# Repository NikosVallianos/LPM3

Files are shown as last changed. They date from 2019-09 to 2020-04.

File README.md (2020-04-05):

# LPM3 front-end #

The LPM3 is a device to measure light pollution on sea turtle nesting beaches. This repository focuses on the development of the front-end of the device, which can be used separately by any programmable device with an I²C and a SPI interface, such as an arduino, raspberry pi, or a suitable USB adapter.

The LPM3 front-end consists of a high sensitivity photometer and a regular sensitivity single-chip lux meter, an accelerometer, and a magnetometer all laid out on a single printed circuit board.

## Ultra-low dark current photodiode

The core of the LPM3 front-end is Hamamatsu's S1133, an ultra-low dark current visible light photodiode. A transimpedance amplifier with a 1GOhm feedback resistor gives a theoretical output of 1V per 0.164 lux. With a 12-bit ADC and a 2.5V reference, we can get a sensitivity of 0.0001 lux. The LPM3 is equipped with a 16-bit ADC, giving an absurd theoretical sensitivity of 0.00000625lux. Imperfections in the circuits and component manufacturing are expected to 

## Generic lux meter

The high sensitivity photodiode circuit is unable to measure any illuminance higher than 0.41lux. For this reason, and to serve as a crude source of self-calubration reference, the OPT3001 single-chip lux meter by Texas Instruments was incorporated in the LPM3 font-end. This lux meter is capable of measurements from 0.01 lux all the way up to daylight. This should cover all foreseeable light pollution conditions from pitch black all the way to in front of spotlights that are sometimes used to safeguard beach equipment.

## Accelerometer

All light pollution measurements should be taken at a horizontal plane, which is where hatchlings and sea turtles scan to perceive ambient light. An embedded accelerometer can either ensure this condition or be used to include device orientation in the dataset.

## Magnetometer

A magnetometer is the only way to know what direction a specific light pollution measurement was taken from.

## License
The LPM3 depository integrates hardware design, firmware source code, desktop software, and supporting documentation. These are licensed as follows:
- Hardware design files are licensed under the CERN Open Hardware License,
- Software source code files are licensed under the GNU GPL v3 license,
- Documentation files are licensed under the GNU Free Documentation License,
- Videos are licensed under Creative Commons Attribution-ShareAlike 4.0 International.

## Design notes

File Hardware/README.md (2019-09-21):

This folder contains the hardware PCB design files, bill of materials, notes, data sheet links, and other details to help you manufacture a LPM3.
The hardware elements of the LPM3 project are licensed under the CERN Open Source Hardware license found here (link missing).

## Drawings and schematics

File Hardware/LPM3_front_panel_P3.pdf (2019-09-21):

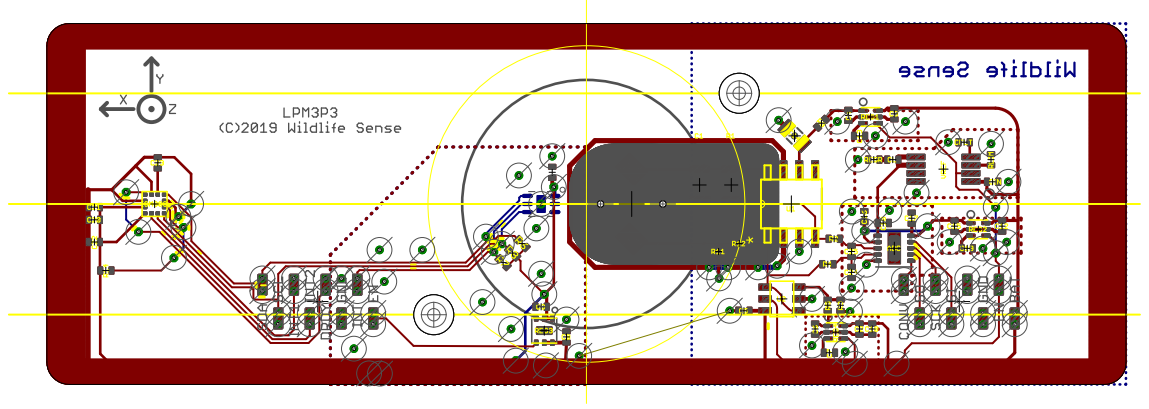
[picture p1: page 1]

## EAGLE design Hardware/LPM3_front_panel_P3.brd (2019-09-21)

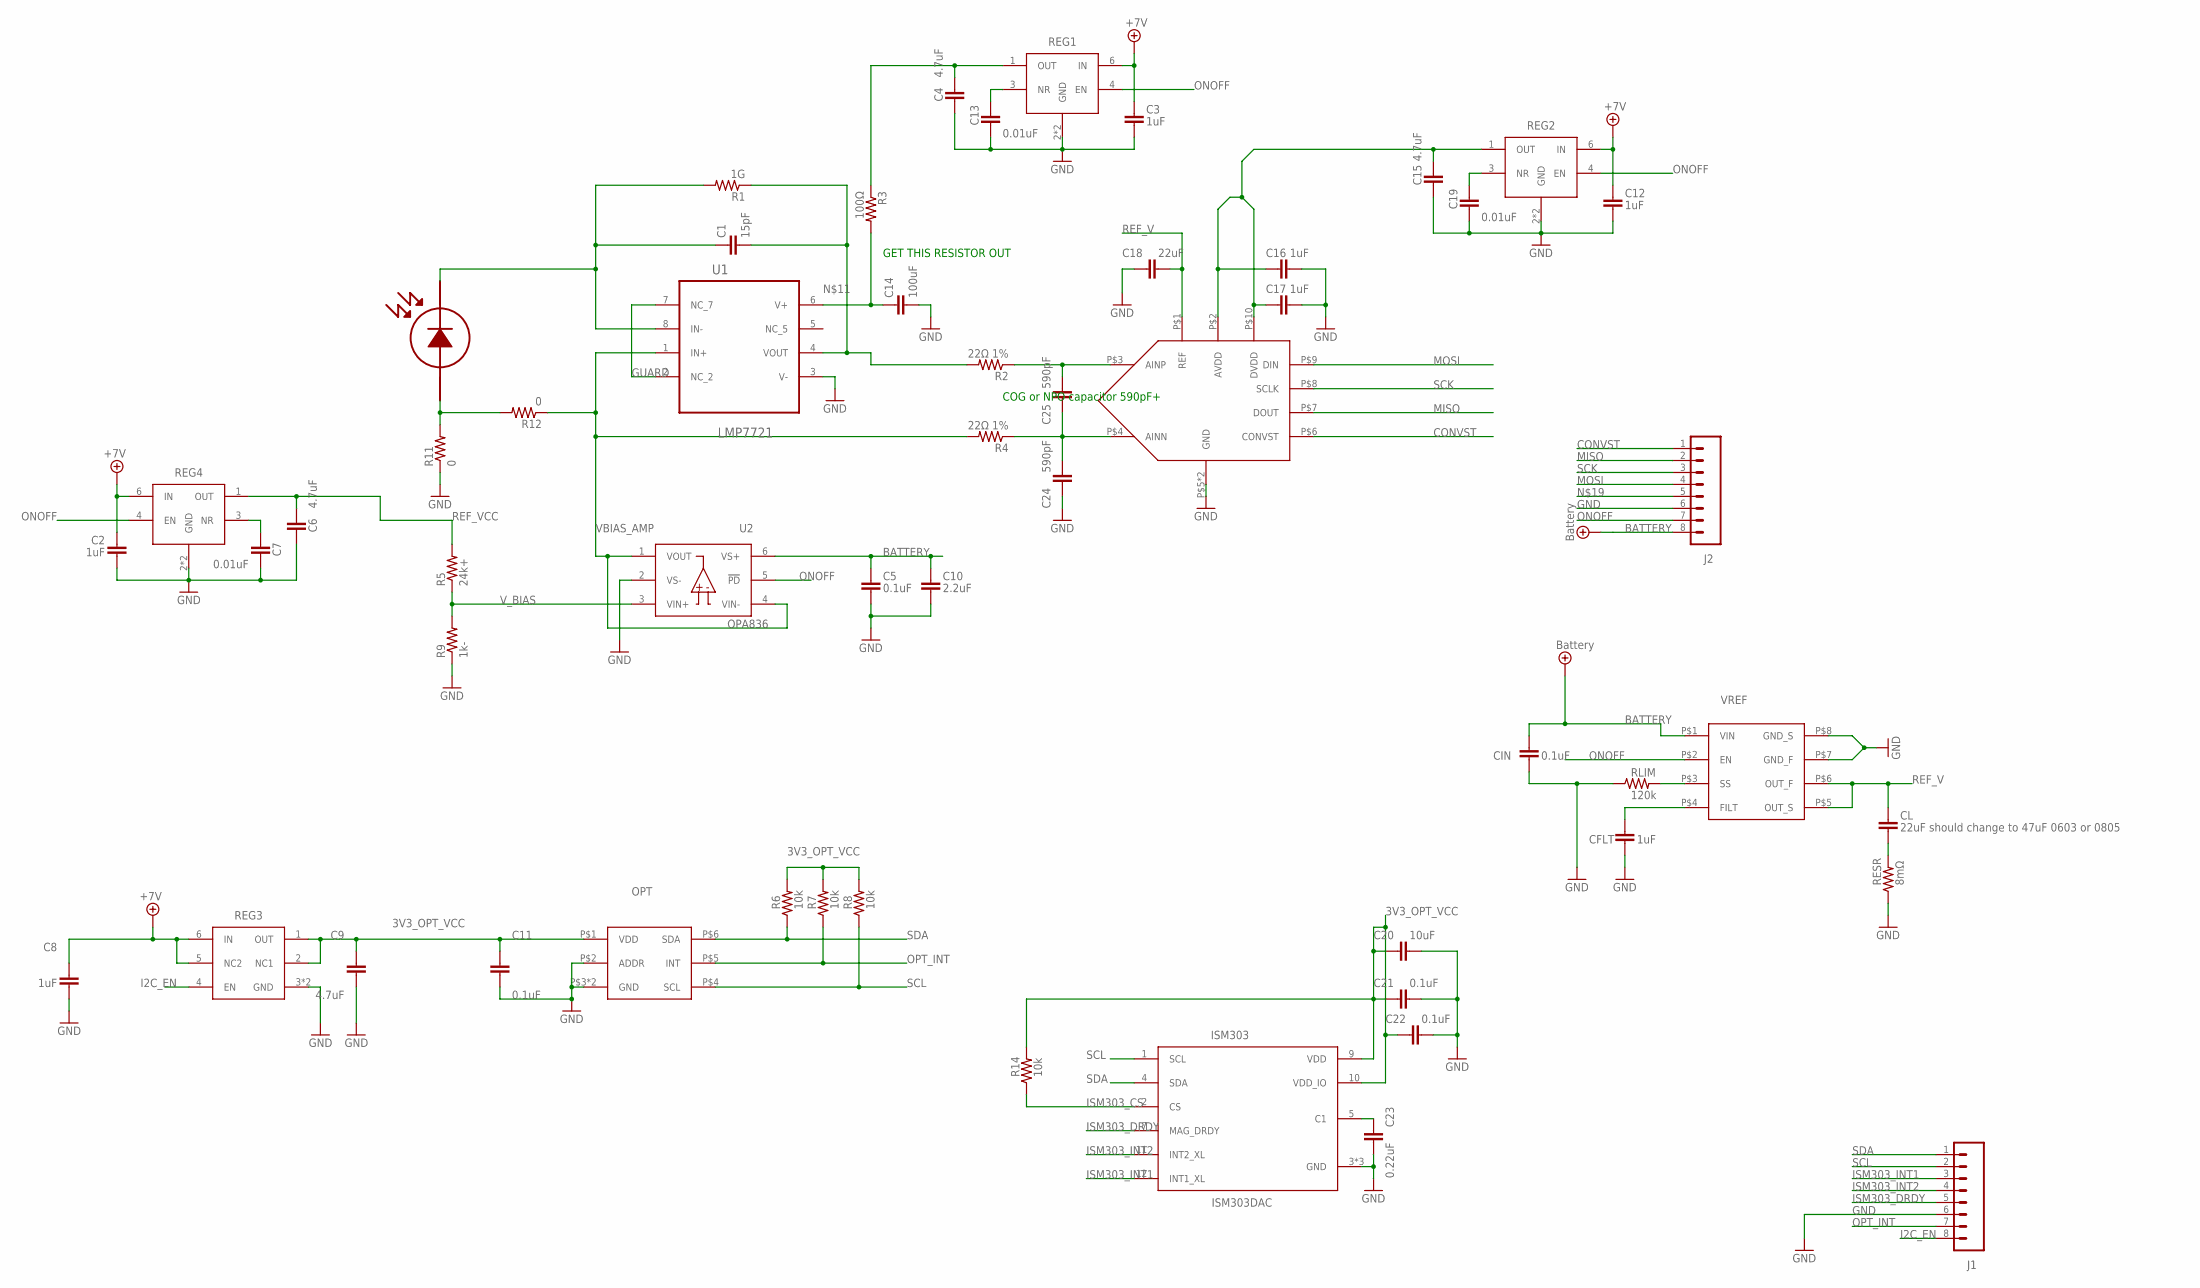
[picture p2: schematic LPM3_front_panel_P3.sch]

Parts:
ADC: ADS8866VSON10; VSON-10
C1: 15pF; 1206
C2, C3, C8, C12, C16, C17: 1uF; SMD_0402
C4, C6, C9, C15: 4.7uF; SMD_0402
C5, C11, C21, C22: 0.1uF; SMD_0402
C7, C13, C19: 0.01uF; SMD_0402
C10: 2.2uF; SMD_0402
C14: 100uF; 0805-CAP
C18: 22uF; SMD_0402
C20: 10uF; SMD_0402
C23: 0.22uF; SMD_0402
C24, C25: 590pF; SMD_0402
CFLT: 1uF; SMD_0402
CIN: 0.1uF; SMD_0402
CL: 22uF should change to 47uF 0603 or 0805; SMD_0402
D1: S1133_3; S1133_FLAT_SIDEWAYS
ISM303: ISM303DAC; LGA_12_ST
J1, J2: 8_PIN_0.05_INCH_SMD_FEMALE; 8_PIN_0.05"_SMD_ALTERN
OPT: OPT3001; USON-6-0.65-OPT3001
R1: 1G; 1206
R2, R4: 22Ω 1%; SMD_0402
R3: 100Ω; SMD_0402
R5: 24k+; SMD_0402
R6, R7, R8, R14: 10k; SMD_0402
R9: 1k-; SMD_0402
R11, R12: 0; SMD_0402
REG1, REG2, REG4: TPS717-Q1; WSON-6-1.5MM-NO-PAD
REG3: TPS706USON-6; USON-6-0.65
RESR: 8mΩ; SMD_0402
RLIM: 120k; SMD_0402
U1: LMP7721; SOIC127P600X175-8N
U2: OPA836; OPA836_SOT23
VREF: REF6225; VSSOP8

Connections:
3V3_OPT_VCC: C9.1, C11.1, C20.1, C21.1, C22.1, ISM303.9 (VDD), ISM303.10 (VDD_IO), OPT.P$1 (VDD), R6.1, R7.1, R8.1, R14.1, REG3.1 (OUT), REG3.2 (NC1)
BATTERY: C2.1, C3.1, C5.1, C8.1, C10.1, C12.1, CIN.1, J2.8, REG1.6 (IN), REG2.6 (IN), REG3.5 (NC2), REG3.6 (IN), REG4.6 (IN), U2.6 (VS+), VREF.P$1 (VIN)
CONVST: ADC.P$6 (CONVST), J2.1
FLT: CFLT.1, VREF.P$4 (FILT)
GND: ADC.P$5 (GND), ADC.P$PAD (GND), C2.2, C3.2, C4.2, C5.2, C6.2, C7.2, C8.2, C9.2, C10.2, C11.2, C12.2, C13.2, C14.2, C15.2, C16.2, C17.2, C18.1, C19.2, C20.2, C21.2, C22.2, C23.2, C24.1, CFLT.2, CIN.2, ISM303.3 (GND), ISM303.6 (GND), ISM303.8 (GND), J1.6, J2.6, OPT.P$2 (ADDR), OPT.P$3 (GND), OPT.PAD (GND), R9.2, R11.2, REG1.2 (GND), REG1.5 (GND), REG2.2 (GND), REG2.5 (GND), REG3.3 (GND), REG3.PAD (GND), REG4.2 (GND), REG4.5 (GND), RESR.2, RLIM.2, U1.3 (V-), U2.2 (VS-), VREF.P$7 (GND_F), VREF.P$8 (GND_S)
GUARD: U1.2 (NC_2), U1.7 (NC_7)
I2C_EN: J1.8, REG3.4 (EN)
ISM303_CS: ISM303.2 (CS), R14.2
ISM303_DRDY: ISM303.7 (MAG_DRDY), J1.5
ISM303_INT1: ISM303.12 (INT1_XL), J1.3
ISM303_INT2: ISM303.11 (INT2_XL), J1.4
MISO: ADC.P$7 (DOUT), J2.2
MOSI: ADC.P$9 (DIN), J2.4
unnamed: ADC.P$3 (AINP), C25.2, R2.2
unnamed: CL.2, RESR.1
unnamed: C1.P$1 (1), D1.CATHODE, R1.P$1 (1), U1.8 (IN-)
unnamed: C19.1, REG2.3 (NR)
unnamed: D1.ANODE, R11.1, R12.1
unnamed: C14.1, R3.1, U1.6 (V+)
unnamed: ADC.P$4 (AINN), C24.2, C25.1, R4.2
unnamed: C23.1, ISM303.5 (C1)
unnamed: C7.1, REG4.3 (NR)
unnamed: C13.1, REG1.3 (NR)
ONOFF: J2.7, REG1.4 (EN), REG2.4 (EN), REG4.4 (EN), U2.5 (!PD!), VREF.P$2 (EN)
OPAMP_VCC: C4.1, R3.2, REG1.1 (OUT)
OPT_INT: J1.7, OPT.P$5 (INT), R7.2
REF_V: ADC.P$1 (REF), C18.2, CL.1, VREF.P$5 (OUT_S), VREF.P$6 (OUT_F)
REF_VCC: C6.1, R5.1, REG4.1 (OUT)
SCK: ADC.P$8 (SCLK), J2.3
SCL: ISM303.1 (SCL), J1.2, OPT.P$4 (SCL), R8.2
SDA: ISM303.4 (SDA), J1.1, OPT.P$6 (SDA), R6.2
SS: RLIM.1, VREF.P$3 (SS)
TIA_OUT: C1.P$2 (2), R1.P$2 (2), R2.1, U1.4 (VOUT)
VBIAS_AMP: R4.1, R12.2, U1.1 (IN+), U2.1 (VOUT), U2.4 (VIN-)
VCC_ADC: ADC.P$2 (AVDD), ADC.P$10 (DVDD), C15.1, C16.1, C17.1, REG2.1 (OUT)
V_BIAS: R5.2, R9.1, U2.3 (VIN+)

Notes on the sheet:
GET THIS RESISTOR OUT
COG or NPO capacitor 590pF+

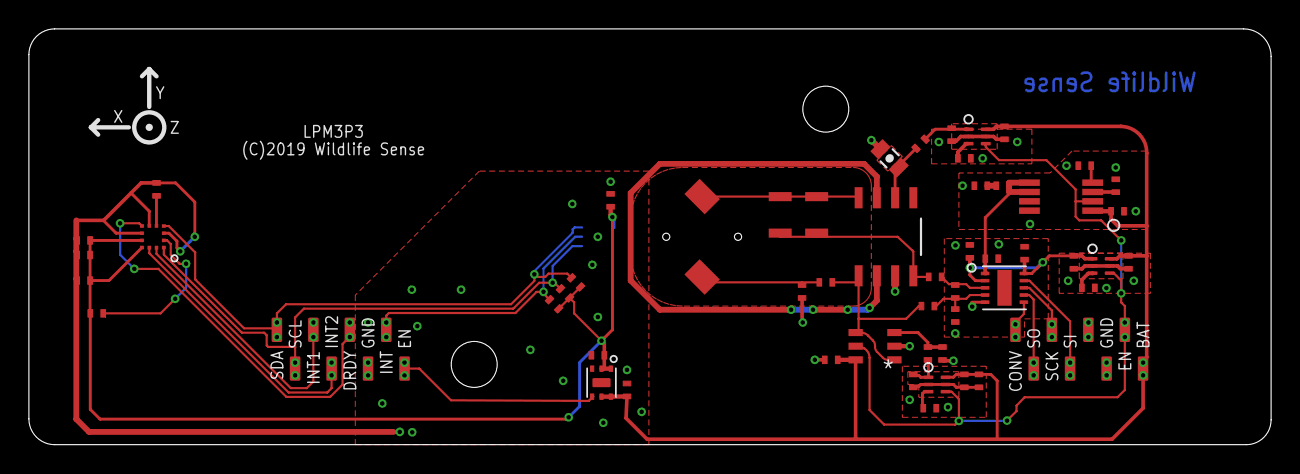
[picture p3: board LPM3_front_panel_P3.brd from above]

Board: 2 copper layers, 86.5 x 29.0 mm, 55 parts (1 on the bottom side), 36 nets.

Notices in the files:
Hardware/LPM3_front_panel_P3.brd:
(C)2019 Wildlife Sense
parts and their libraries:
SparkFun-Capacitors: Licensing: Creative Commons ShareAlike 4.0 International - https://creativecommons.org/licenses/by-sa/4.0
